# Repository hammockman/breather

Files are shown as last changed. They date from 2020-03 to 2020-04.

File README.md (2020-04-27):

This repository contains design details for a cheap easy to build and source ventilator.
this design was completed as part of competition in response to COVID-19 (see link below for competion info)
(https://www.agorize.com/en/challenges/code-life-challenge)

Since COVID-19 there have been a large increase in the number of open source ventilator designs. the links below are useful resources for someone who is wanting to design and or build an emergency ventilator in response to some sort of pandemic event such as COVID-19.

Links:

[Corona Virus Tech Handbook. Ventilator Chapter.] (https://coronavirustechhandbook.com/ventilators)

[Github Repository with a large number of existing design links] (https://github.com/eellak/covid19-open/blob/master/Hardware.md)

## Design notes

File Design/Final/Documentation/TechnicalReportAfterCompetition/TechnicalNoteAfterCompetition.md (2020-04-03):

---
title: "Manawa Ora"
subtitle: "Technical Note after Agorize submission"
author: [Manawa Ora team]
date: 2020-04-03
titlepage: true
toc: true
toc-own-page: true
tags: [ventilator, agorize]
...

# Summary

This note is a collection of documents that were part of the submission in the
Agorize Competition: "Code Life Ventilator Challenge". The team name for that
competition was *Manawa Ora*, and that name is also used herein for the team and
the design.

Our design goals were to make and design a simple ventilator that:

 - could be made anywhere in the world
 - used parts with supply chains outside the medical industry

Our main constraint was that we started the design only a couple of days before New
Zealand went into lock-down, and therefore only had the parts we'd bought the day
before stores closed.

The current version has the following "features":

 - 1" (25mm) BSP irrigation fittings provide gas conveyance, structural
   integrity, and sensor housing. These can be purchased from local suppliers in
   (plastic or stainless steel) or 3D-printed.

 - Air and oxygen flow are sensed using automotive Mass Air Flow Sensors. The
   ratio of these flows provides measurement of FiO2.

 - An expiration valve closes during inspiration and when expiration pressure
   falls below PEEP. High PEEP pressures can be provided by introducing small
   amounts of air via the inspriation valves.

 - The valving logic removes the need for a flap valve at the Y-piece.

 - Wireless communication of measured data and control commands. This allows for
   multiple viewers (e.g. tablet, PC, centralised PC, decentralised).

 - Filters and humidifier are separate units.

The design relies on the supply of clean compressed air and oxygen. This choice
has been made to a) keep the machine simple, and b) because we think large
gas banks and/or compressors are a more efficient way to supply several or many
ventilators.

\newpage
## Status

The prototype is built and satisfies most of the Agorize competition goals. It
is, however, not ready for production. The big picture of outstanding work follows:

Missing/incomplete feature | Difficulty
--|--
Add alarms to code and GUI | Simple
Sort required security for wireless communication and control | Depends on reuirements
Add correct fittings for hospital air/O2 supply | Simple
Improve flutter in valve control | Medium
Improve/test PEEP control when there is vacuum connected to expiration exhaust |Medium
Add a 230 v plug and main switch | Simple

Many of these aspects could be improved by having technical support from
appropriately trained and experienced medical personnel.

# Design

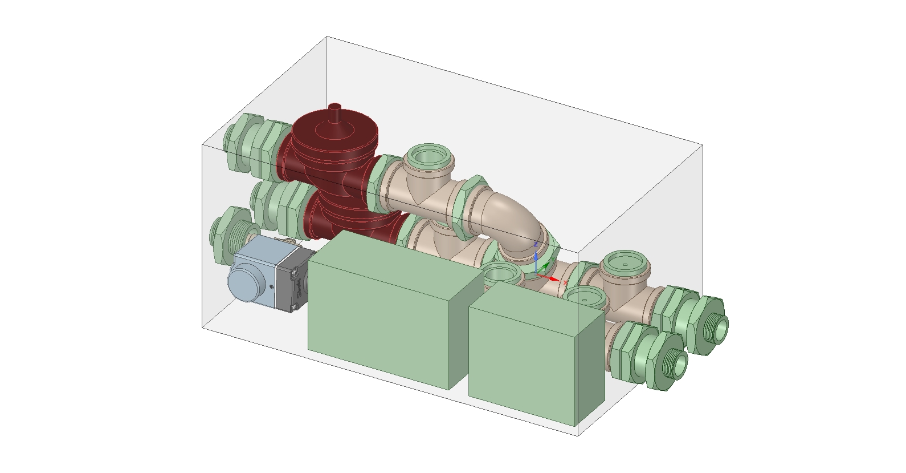
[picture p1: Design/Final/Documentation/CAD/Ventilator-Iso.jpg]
Isometric depiction of ventilator. The cabinet is semi-transparent, and the two ports on the front of the machine are the patient-side inspiration (right) and expiration (left) ports


Layout of the proposed ventilator

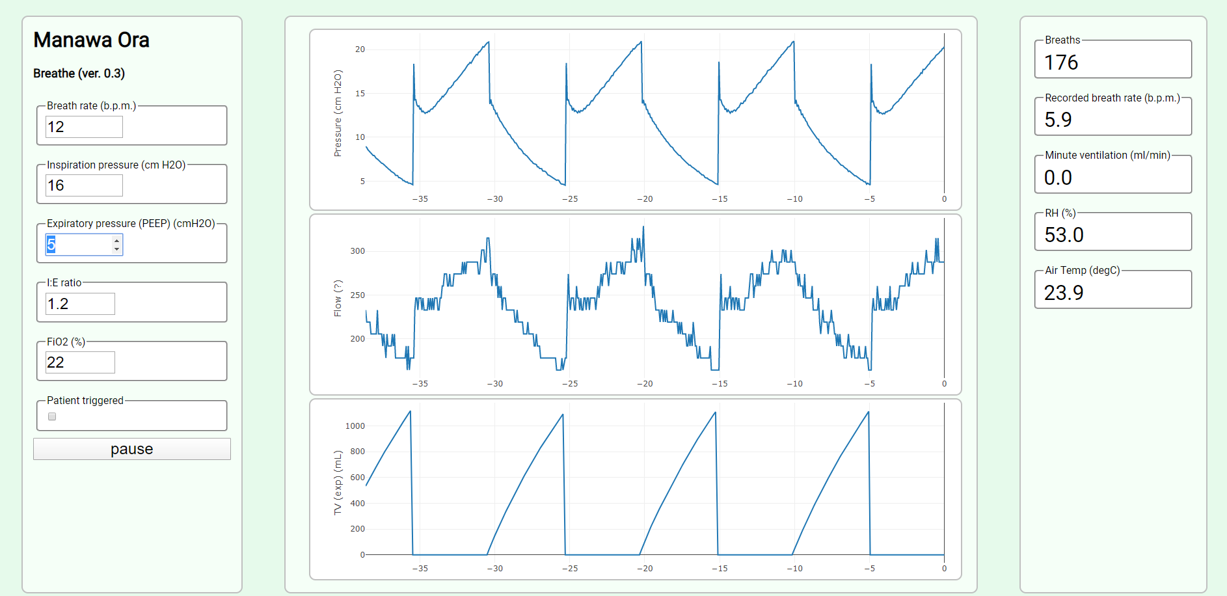
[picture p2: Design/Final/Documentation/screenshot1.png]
Operator user interface. The unit does not have any screen of it's own: it relies on wireless communication to other computers and devices.


# Prototype

The following two photos show the prototype that was made.

![Ventilator prototype. The rear of the machine is in the foreground: air inlet,
oxygen inlet, expriation exhaust. The middle ground shows the inspiration and
expiration conveyances, sensors, and electronics. In the background is the
tidal volume calibration (EasyYo) containers, the patient, and the bubble
humidifier. The patient is simulated by a dry bag restrained by a weighted and
sprung plywood hinge. Patient compliance is reduced by increasing the spring stiffness.](../system_with_pi1.jpg)

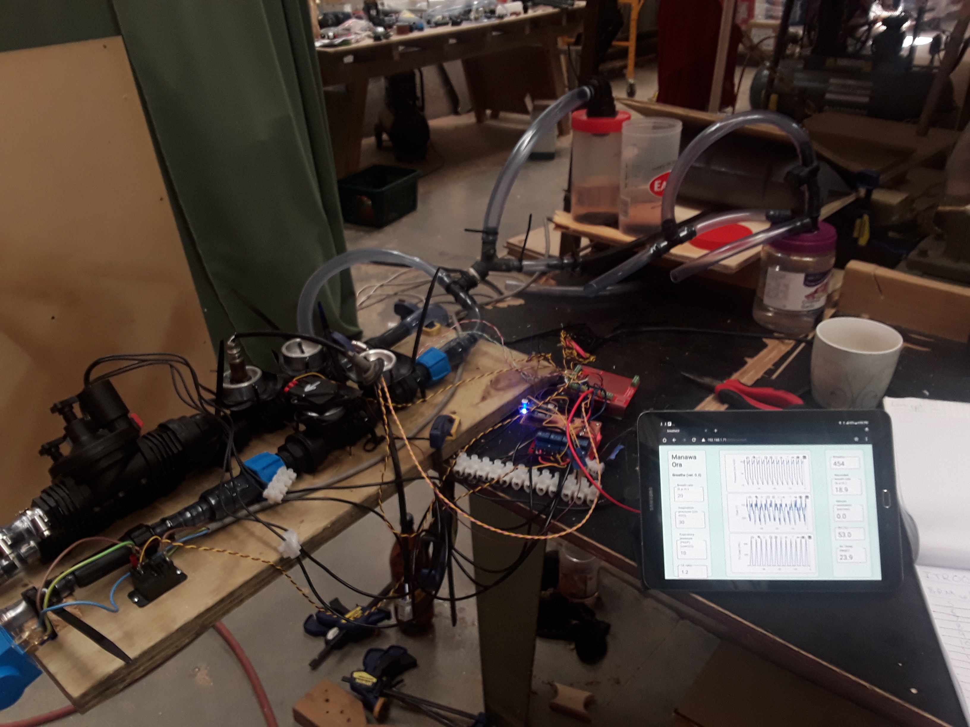
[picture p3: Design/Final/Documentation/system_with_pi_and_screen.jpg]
Operator interface on a tablet


\newpage
# Appendices

\newpage

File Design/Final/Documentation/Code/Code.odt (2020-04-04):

Manawa Ora software

## Overview and user guide

The Manawa-Ora codebase comprises two parts:

1. The User Interface software that allows the user to read and control the ventilator using a web browser. The browser can be on a tablet or central PC
2. The code on the mini-computer inside the ventilator is written using python. The software starts automatically and the normal user does not have to do any setup.

The user interface is shown below:

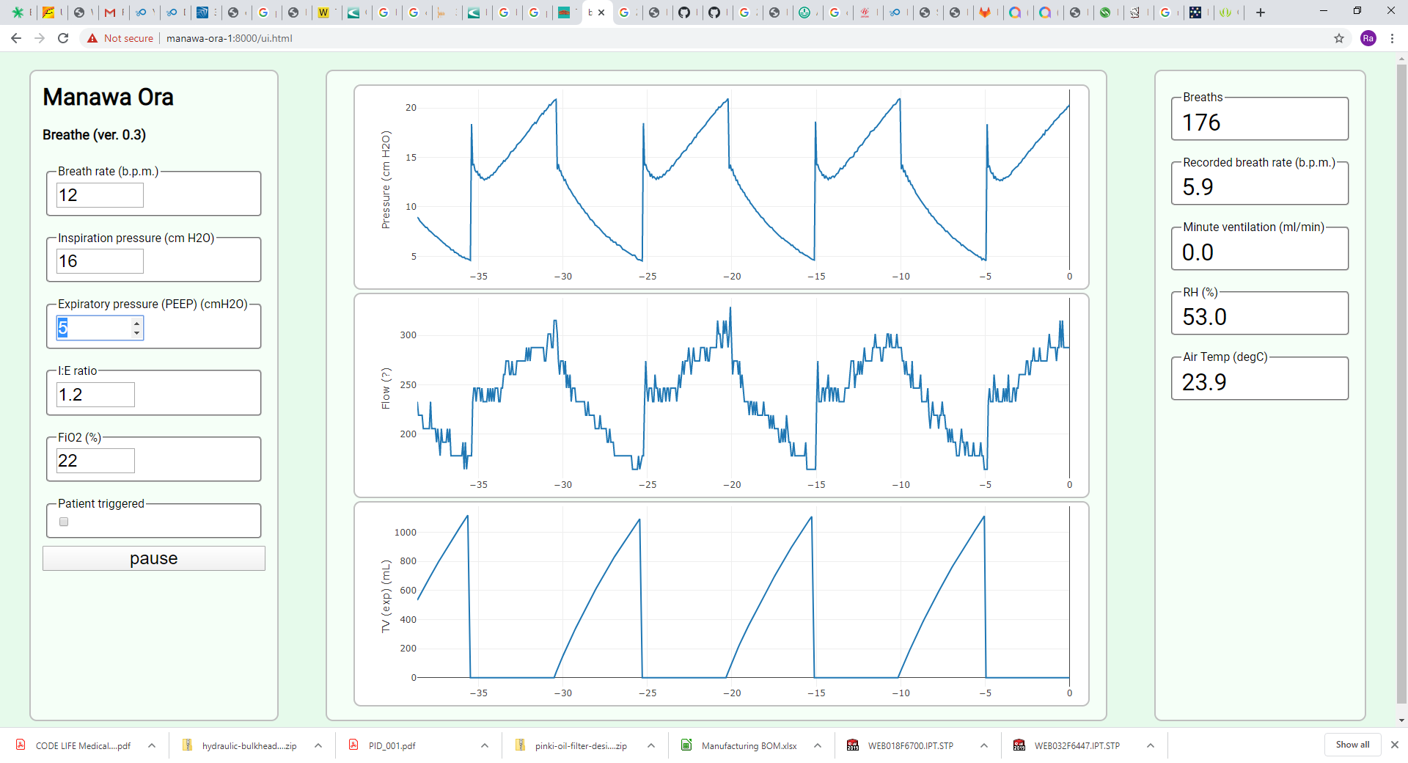
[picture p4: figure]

The operator can modify settings using the menu in the left panel. Resulting ventilation graphs and readings are shown in the centre and right hand panels.

# Installation

To install the ventilator for the first time the cabinet must be opened and an ethernet cable attached to the controller and a facility IT professional must assign the computer a static IP address: a ventilator ID should (preferably) be given as the machine hostname.

To install the User Interface software:

- The device browser, on a tablet or PC, needs to point to the IP address or hostname.

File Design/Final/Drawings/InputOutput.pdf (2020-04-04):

Sheet1

Page 1

Function | Tag | Instrument | I/O | PI address | Bus | PI Terminal
Inspiration pressure / temperature sensor | PT-011 | | | | I2C-1 | 3, 5
Temp / humidity sensor | HT-011 | | | | | 4
Expiration pressure / temperature sensor | PT-021 | | | | I2C-4 | 24,25
Air flow sensor | FT-011 | | analogue in | | A-D card | 3, 5
Oxygen flow sensor | FT-012 | | analogue in | | A-D card | 3, 5
Expiration flow sensor | FT-021 | | analogue in | | A-D card | 3, 5
Air inlet valve | SV-011 | R1 relay board | digital out | | | 17
Oxygen inlet valve | SV-012 | R2 relay board | digital out | | | 18
Expiration valve | SV-021 | R3 relay board | digital out | | | 25

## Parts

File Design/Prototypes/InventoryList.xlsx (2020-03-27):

Item Desc. | Part number | Domain | Supplier | Status | Quantity | unit price | cost | Puchased by
SG-5010 4.8-6V Servo Motor | SG-5010 | ` | Jaycar | received | 1 | 24.9 | 24.9 | JJ
2008 MAZDA 6 AIR FLOW METER |  | Sensor | maztech | awaiting delivery | 1 | 69 | 69 | JJ
2003 MAZDA MPV EGR VALVE |  | Sensor | maztech | awaiting delivery | 1 | 51.75 | 51.75 | JJ
2004 MAZDA 3 AIR CLEANER BOX |  | Filter | maztech | awaiting delivery | 1 | 46 | 46 | JJ
PVC Clear Tube - 7.9mm |  | Piping | irrigation express | awaiting delivery | 2 | 1.42 | 2.84 | JJ
PVC Clear Tube - 9.5mm |  | Piping | irrigation express | awaiting delivery | 2 | 2 | 4 | JJ
PVC Clear Tube - 13mm |  | Piping | irrigation express | awaiting delivery | 2 | 2.98 | 5.96 | JJ
PVC Clear Tube - 16mm |  | Piping | irrigation express | awaiting delivery | 2 | 3.82 | 7.64 | JJ
PVC Clear Tube - 19mm |  | Piping | irrigation express | awaiting delivery | 2 | 5.68 | 11.36 | JJ
PVC Clear Tube - 25mm |  | Piping | irrigation express | awaiting delivery | 2 | 9.38 | 18.76 | JJ
Antelco Lateral Tees - 13mm |  | Piping | irrigation express | awaiting delivery | 2 | 0.33 | 0.66 | JJ
Antelco Lateral Tees - 16mm |  | Piping | irrigation express | awaiting delivery | 2 | 0.78 | 1.56 | JJ
Antelco Lateral Tees - 19mm |  | Piping | irrigation express | awaiting delivery | 2 | 0.45 | 0.9 | JJ
Antelco Lateral Tees - 25mm |  | Piping | irrigation express | awaiting delivery | 2 | 0.92 | 1.84 | JJ
Antelco Lateral Tees 4mm - 10mm - 10mm |  | Piping | irrigation express | awaiting delivery | 2 | 0.92 | 1.84 | JJ
Antelco Lateral Valves (Green Back) - 16mm |  | Piping | irrigation express | awaiting delivery | 3 | 2.46 | 7.38 | JJ
Dripline Ratchet Clip 16mm |  | Piping | irrigation express | awaiting delivery | 12 | 0.24 | 2.88 | JJ
Norma 9mm S/Steel Band Worm Drive Hose Clamps - 8mm - 12mm |  | Piping | irrigation express | awaiting delivery | 8 | 1.9 | 15.2 | JJ
Norma 9mm S/Steel Band Worm Drive Hose Clamps - 16mm - 25mm |  | Piping | irrigation express | awaiting delivery | 8 | 1.9 | 15.2 | JJ
Dripline to Lateral Reducing Joiner - 16mm/13mm |  | Piping | irrigation express | awaiting delivery | 4 | 0.47 | 1.88 | JJ
Dripline to Lateral Reducing Joiner - 19mm/16mm |  | Piping | irrigation express | awaiting delivery | 4 | 0.47 | 1.88 | JJ
Dripline to Lateral Reducing Joiner - 25mm/16mm |  | Piping | irrigation express | awaiting delivery | 4 | 1.08 | 4.32 | JJ
16mm Dripline Elbow |  | Piping | irrigation express | awaiting delivery | 2 | 0.28 | 0.56 | JJ
Lateral Inline Screen Filter - 13mm - 19mm - 16mm |  | Piping | irrigation express | awaiting delivery | 2 | 5.19 | 10.38 | JJ
50mm Plastic display side entry 8mm Pressure Gauge - 35psi 2.5Bar plastic side entry Pressure Gauge |  | Piping | irrigation express | awaiting delivery | 1 | 8.5 | 8.5 | JJ
Hansen Reducing Bush - 15mm/8mm |  | Piping | irrigation express | awaiting delivery | 1 | 1.85 | 1.85 | JJ
Antelco Female Threaded Tee - Threaded Tee - 13mm Barbs x 15mm BSPF |  | Piping | irrigation express | awaiting delivery | 1 | 2.01 | 2.01 | JJ
Antelco Female Threaded Tee - Threaded Tee - 19mm Barbs x 15mm BSPF |  | Piping | irrigation express | awaiting delivery | 1 | 1.66 | 1.66 | JJ
Antelco Female Threaded Tee - Threaded Tee - 25mm Barbs x 15mm BSPF |  | Piping | irrigation express | awaiting delivery | 1 | 1.87 | 1.87 | JJ
MULTICOMP HCZ-D5-A Humidity Sensor, HCZ Series, 20% to 90% RH, 5 %, Through Hole, Enclosed |  | Sensor | element 14 | awaiting delivery | 2 | 9.98 | 19.96 | JJ
OMRON 2SMPP-02 Pressure Sensor, MEMS, Air, 0 to 50°C, 37 kPa, Voltage, Gauge, Hose / Tube, 100 µA |  | Sensor | element 14 | awaiting delivery | 4 | 5.16 | 20.64 | JJ
MULTICOMP PRO MC6A-7/0.2T2-PK-100M Wire, Stranded, Equipment, 7/0.2 mm Type 2, Per Metre, PVC, Pink, 0.22 mm² |  | Wiring | element 14 | awaiting delivery | 5 | 0.301 | 1.505 | JJ
MULTICOMP PRO MC6A-7/0.2T2-BN-100 Wire, Stranded, Equipment, 7/0.2 mm Type 2, Per Metre, PVC, Brown, 0.22 mm² |  | Wiring | element 14 | awaiting delivery | 5 | 0.301 | 1.505 | JJ
MULTICOMP PRO MC6A-7/0.2T2-YW-100 Wire, Stranded, Equipment, 7/0.2 mm Type 2, Per Metre, PVC, Yellow, 0.22 mm² |  | Wiring | element 14 | awaiting delivery | 5 | 0.301 | 1.505 | JJ
MULTICOMP PRO MC6A-1/0.6T2-PK-100 Wire, Solid, Equipment, Per Metre, PVC, Pink, 23 AWG, 0.28 mm² |  | Wiring | element 14 | awaiting delivery | 5 | 0.378 | 1.89 | JJ
MULTICOMP PRO MC6A-1/0.6T2-YW-100 Wire, Solid, Equipment, Per Metre, PVC, Yellow, 23 AWG, 0.28 mm² |  | Wiring | element 14 | awaiting delivery | 10 | 0.356 | 3.56 | JJ
Fuel filter inline 3/8 |  | Filter | BNT | received | 2 | 18 | 36 | RC
240v washing machine solenoid valve |  | Valve | Philip smith | received | 1 | 25 | 25 | RC
240v refrigerant solenoid valve |  | Valve | Philip smith | received | 1 | 145 | 145 | RC
Air flow sensor |  | Sensor | Repco | received | 1 | 252.75 | 252.75 | RC
Vacuum hose t-junction 10mm |  | Piping | Repco | received | 2 | 10.87 | 21.74 | RC
Oxygen sensor |  | Sensor | Repco | received | 1 | 93 | 93 | RC
Temp/Humidity sensor |  | Sensor | Jaycar | received | 1 | 11.9 | 11.9 | RC
Laser diode |  | Sensor | Jaycar | received | 1 | 6.9 | 6.9 | RC
Digital barometric pressure sensor |  | Sensor | Jaycar | received | 2 | 22.9 | 45.8 | RC
Battery SLA 12v 6Ah |  | Battery | Jaycar | received | 1 | 36.9 | 36.9 | RC
DC-DC voltage regulator (variable) |  | Electronics | Jaycar | received | 1 | 10.9 | 10.9 | RC
Relay board 5V |  | Electronics | Jaycar | received | 2 | 6.9 | 13.8 | RC
Relay board 4 ch 12v |  | Electronics | Jaycar | received | 1 | 17.9 | 17.9 | RC
Raspberry Pi 3B+ |  | Electronics | Jaycar | received | 1 | 99.9 | 99.9 | RC
Raspberry Pi prototyping shield |  | Electronics | Jaycar | received | 1 | 17.9 | 17.9 | RC
Raspberry Pi touch LCD |  | Electronics | Jaycar | received | 1 | 56.9 | 56.9 | RC
Raspberry Pi GPIO expansion |  | Electronics | Jaycar | received | 1 | 16.9 | 16.9 | RC
PCB prototyping board |  | Electronics | Jaycar | received | 2 | 5.9 | 11.8 | RC
Air hose 10mm |  | Piping | Tradezone | received | 2 | 5 | 10 | RC
Pneumatic T-junctions 10mm |  | Piping | Tradezone | received | 4 | 2 | 8 | RC
12V 25mm normally closed solenoid valves (SV25-12) |  | Valve | The Water Sprinkler Shop | awaiting delivery | 2 | 30.36 | 60.72 | JH
12V 25mm latching/pulse valves (SV25L) |  | Valve | The Water Sprinkler Shop | awaiting delivery | 2 | 36.68 | 73.36 | JH
12V Solenoid Coil (SC2-12) |  | Valve | The Water Sprinkler Shop | awaiting delivery | 2 | 15.39 | 30.78 | JH
25mm BSP Female Elbow (7208/25) |  | Piping | The Water Sprinkler Shop | awaiting delivery | 8 | 2.25 | 18 | JH
25mm BSP Female Tee (T25F) |  | Piping | The Water Sprinkler Shop | awaiting delivery | 6 | 2.97 | 17.82 | JH
25mm BSP Male Nipple (NP-25) |  | Piping | The Water Sprinkler Shop | awaiting delivery | 12 | 0.91 | 10.92 | JH
25mm-15mm BSP Reducing Male Nipple (?) |  | Piping | The Water Sprinkler Shop | awaiting delivery | 3 | 2.15 | 6.45 | JH
12V Airtac Solenoid valve | 4V110-06 | Valve | Edwin | received | 5 | ?? |  | Edwin
One touch plastic pneumatic fitting t type 6mm quick tube connector air 3 way PE-6 union pipe joint |  | Piping | Aliexpress | received | 10 | ?? | ?? | Edwin
Air Pneumatic 10mm Hose Tube ??? Male Thread Air Pipe Connector Quick Coupling Brass Fitting |  | Piping | Aliexpress | received | 10 | ?? | ?? | Edwin
Potter and Brumfield 12 V relay NO and NC 230 V contacts | T9AP5D52-12 | Electronics | ?? | received | 2 | ?? | ?? | Edwin
Potter and Brumfield 12 V relay NO 230 V contacts | T9AP1D52-12 | Electronics | ?? | received | 2 | ?? | ?? | Edwin
12V relay from the dark ages with 4 sets of contacts |  | Electronics | ?? | received | 1 | ?? | ?? | Edwin

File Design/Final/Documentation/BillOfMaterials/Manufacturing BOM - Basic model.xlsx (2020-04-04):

MANUFACTURING BOM – Basic model
ITEM | DESCRIPTION | PART NUMBER | QTY | UNIT COST | NZ SUPPLIER | PRICE (NZD) | Price (USD) | Supply industry
1 | 25mm BSP Female Tee | (T25F) | 3 | 2.97 | The Water Sprinkler Shop | 8.91 | 5.35 | Irrigation/plumbing
2 | 25mm BSP Female Elbow | (7208/25) | 2 | 2.25 | The Water Sprinkler Shop | 4.50 | 2.70 | Irrigation/plumbing
3 | 25mm BSP Male Nipple | (NP-25) | 6 | 0.91 | The Water Sprinkler Shop | 5.46 | 3.28 | Irrigation/plumbing
4 | 12V 25mm normally closed solenoid valves | (SV25-12) | 2 | 30.36 | The Water Sprinkler Shop | 60.72 | 36.43 | Irrigation/plumbing
5 | 25x15mm Reducing Bush | HRB2515 | 4 | 1.77 | Irrigation Express | 7.08 | 4.25 | Irrigation/plumbing
6 | Tank fittings | HTFFT25 | 4 | 7.41 | Irrigation Express | 29.64 | 17.78 | Irrigation/plumbing
7 | Solenoid valve, EVR 6 - normally open | 032L8085 | 1 | 72.5 | Philip Smith | 72.50 | 43.50 | Electrical supplies
8 | Solenoid coil, BE230AS | 018F6701 | 1 | 72.5 | Philip Smith | 72.50 | 43.50 | Electrical supplies
9 | Large particle filter | 8-16/9W4P | 1 | 1.9 | Irrigation Express | 1.90 | 1.14 | Irrigation/plumbing
10 | Temp/Humidity sensor | DHT12 | 1 | 14.9 | Jaycar | 14.90 | 8.94 | Electronic supplies
11 | Digital barometric pressure sensor | BMP180 | 2 | 22.9 | Jaycar | 45.80 | 27.48 | Electronic supplies
12 | Raspberry Pi 3B+ | 3B+ | 1 | 65 | Jaycar | 65.00 | 39.00 | Electronic supplies
13 | Raspberry Pi shield and ADC | XC9050 | 1 | 17.9 | Jaycar | 17.90 | 10.74 | Electronic supplies
14 | Raspberry Pi GPIO expansion | XC9040 | 1 | 16.9 | Jaycar | 16.90 | 10.14 | Electronic supplies
15 | Relay board 4 ch 12v | XC4419 | 1 | 17.9 | Jaycar | 17.90 | 10.74 | Electronic supplies
16 | PS with battery SLA 12v 6Ah | SB2485 | 1 | 36.9 | Jaycar | 36.90 | 22.14 | Electronic supplies
17 | DC-DC voltage regulator (variable) | XC4514 | 1 | 10.9 | Jaycar | 10.90 | 6.54 | Electronic supplies
18 | Fuelmiser Air Flow Sensor | VDO - CAF034 | 2 | 40 | Repco | 80.00 | 48.00 | Automotive parts warehouse
19 | Cabinet | 22” toolbox | 1 | 30 | Bunnings | 40.00 | 24.00
 |  |  |  | Total cost |  | 609.41 | 365.65

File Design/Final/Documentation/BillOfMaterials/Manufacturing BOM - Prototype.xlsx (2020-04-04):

MANUFACTURING BOM – Prototype as built
ITEM | DESCRIPTION | PART NUMBER | QTY | UNIT COST | NZ SUPPLIER | PRICE (NZD) | Price (USD)
1 | 25mm BSP Female Tee | (T25F) | 3 | 2.97 | The Water Sprinkler Shop | 8.91 | 5.35
2 | 25mm BSP Female Elbow | (7208/25) | 1 | 2.25 | The Water Sprinkler Shop | 2.25 | 1.35
3 | 25mm BSP Male Nipple | (NP-25) | 5 | 0.91 | The Water Sprinkler Shop | 4.55 | 2.73
4 | 25mm Hex Screw Plug | HSP25 | 3 | 0.87 | Irrigation Express | 2.61 | 1.57
5 | 12V 25mm normally closed solenoid valves | (SV25-12) | 2 | 30.36 | The Water Sprinkler Shop | 60.72 | 36.43
6 | 15x6mm Reducing Bush | HRB1506 | 2 | 1.19 | Irrigation Express | 2.38 | 1.43
7 | 25x15mm Reducing Bush | HRB2515 | 5 | 1.77 | Irrigation Express | 8.85 | 5.31
8 | 15mm Male Hose Tail | HHT15 | 3 | 2.13 | Irrigation Express | 6.39 | 3.83
9 | 16mm End Plug | LEP16 | 1 | 1.16 | Irrigation Express | 1.16 | 0.70
10 | 16mm Lateral Inline Filter | LILF16 | 2 | 5.19 | Irrigation Express | 10.38 | 6.23
11 | Solenoid valve, EVR 6 - normally open | 032L8085 | 1 | 72.5 | Philip Smith | 72.50 | 43.50
12 | Solenoid coil, BE230AS | 018F6701 | 1 | 72.5 | Philip Smith | 72.50 | 43.50
13 | PVC Clear Tube - 16mm - per meter | PVC-30-1016 | 1 | 3.82 | Irrigation Express | 3.82 | 2.29
14 | 8mm – 16mm Worm Drive Hose Clamp | 8-16/9W4P | 2 | 1.9 | Irrigation Express | 3.80 | 2.28
15 | Norma 9mm S/Steel Hose Clamps – 16mm-25mm | 16-25/9W4P | 12 | 1.9 | Irrigation Express | 22.80 | 13.68
16 | Mechpro Connector 1/4in M | MPC14M | 3 | 6.49 | Repco | 19.47 | 11.68
17 | O2 Sensor | AFR722-EE26 | 1 | 93 | Repco | 93.00 | 55.80
18 | Temp/Humidity sensor | DHT11 | 1 | 11.9 | Jaycar | 11.90 | 7.14
19 | Digital barometric pressure sensor | BMP180 | 2 | 22.9 | Jaycar | 22.90 | 13.74
20 | Raspberry Pi 3B+ | 3B+ | 1 | 99.9 | Jaycar | 99.90 | 59.94
21 | Raspberry Pi shield and ADC | XC9050 | 1 | 17.9 | Jaycar | 17.90 | 10.74
22 | Raspberry Pi GPIO expansion | XC9040 | 1 | 16.9 | Jaycar | 16.90 | 10.14
23 | Relay board 4 ch 12v | XC4419 | 1 | 17.9 | Jaycar | 17.90 | 10.74
24 | Battery SLA 12v 6Ah | SB2485 | 1 | 36.9 | Jaycar | 36.90 | 22.14
25 | DC-DC voltage regulator (variable) | XC4514 | 1 | 10.9 | Jaycar | 10.90 | 6.54
26 | Fuelmiser Air Flow Sensor | VDO - CAF034 | 1 | 252.75 | Repco | 252.75 | 151.65
 |  |  |  | Total cost |  | 884.04 | 530.42

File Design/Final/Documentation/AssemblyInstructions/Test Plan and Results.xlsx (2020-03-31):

Inspection Test Plan
Date Created | 2020-01-31
Project | Ventilator
Created By | Joseph Jury
Item |  | Completed By | Witnessed By | Date | Reference Documents | Results | Notes

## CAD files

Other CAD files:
Design/Final/Drawings/VentElec1.dwg

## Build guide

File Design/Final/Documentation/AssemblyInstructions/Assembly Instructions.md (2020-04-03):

# Assembly instructions

1.  Assemble pipe fittings and solenoid valves for inspiratory line as
    per MO-GA001. Take care to ensure thread tape is used on all male
    threads. Tighten fittings hand tight and then a further 3/4 turn or
    more using a spanner.

2.  Assemble pipe fittings and solenoid valve for expiratory line as per
    MO-GA001. Take care to ensure thread tape is used on all male
    threads. Tighten fittings hand tight and then a further 3/4 turn or
    more using a spanner.

3.  Lower expiratory line into housing. Mount tank fittings onto housing
    and expiratory line as per MO-GA001.

4.  Lower inspiratory line into housing. Mount Tank fittings onto
    housing and inspiratory line as per MO-GA001.

5.  Mount all sensors in T-junctions as per MO-GA001 & MO-PID-001.
    Ensure sensors are mounted using correctly modified 1" BSP blanking
    plugs.

6.  Mount 'raspberry pi controller', '12V Relay Board', '12-5V DC-DC'
    converter and '230V AC 12V DC UPS' as per MO-E-001

7.  Mount the above electrical controls into ventilator housing as per
    MO-GA001

1.  Connect solenoid valves and flow sensors to 12V Relay Board as per
    MO-E-001 & MO-PID-001

2.  Connect humidity and pressure sensors to 5V rail on Raspberry Pi
    Controller as per MO-E-002 & MO-PID-001

3.  Once device has been fully assembled. Consult MO-ITP-001 for Factory
    acceptance testing

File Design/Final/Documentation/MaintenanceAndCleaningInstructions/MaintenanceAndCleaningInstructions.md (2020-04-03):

# Maintenance and cleaning instructions

Cleaning
========

Exterior
--------

1.  Disconnect hoses and filters
2.  Wipe the outside of the cabinet with a damp clean cloth. Light
    solvents and detergents may be used

Interior
--------

1.  Clean the exterior, do not connect hoses until interior cleaning is
    complete
2.  Connect a 22mm hose to the expiration connector on the front of the
    unit
3.  Connect the expiration connector at the rear of the unit to a
    watertight receptacle
4.  If a flow sensor is fitted to the expiration channel (this is an
    optional extra), then this sensor must be removed prior to the
    following step. Also prior to the following step, screw the supplied
    blind fitting in place of the flow sensor.
5.  Flush ten (10) litres of water-disinfectant solution through, from
    the front to the rear, of the expiration channel
6.  NEVER FLUSH LIQUIDS THROUGH THE INSPIRATION SIDE OF THE MACHINE.

Maintenance
===========

1.  The filters and humidifier are external to the unit and should be
    maintained/replaced as required by the manufacturer
2.  The 12v solenoids should be replaced every 4000 hours.

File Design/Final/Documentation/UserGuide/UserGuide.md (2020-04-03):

--var fio2: FiO<sub>2</sub>
--var vent: Manawa Ora

# {{vent}} User Guide

## Revision History

| Version | Date | Author(s) |
| ------- | ---- | ----------|
| v0.1 | 01/04/20 | JH, RC, JJ, MO |

## Contact Details

**Manawa Ora**
385 State Highway 33
Mourea
Rotorua 3074
New Zealand

Customer Care:
manawaoraservice@aliente.ch

## Warranty

There are no warranties expressed or implied.

Manawa Ora shall not be liable for loss of profits, loss of use, consequential damages, or any other
claim based on breach of warranty. Manawa Ora liability for damages of any kind shall be limited to the
purchase price of the defective unit.

## Notices

The {{vent}} ventilator complies with XXX. It does however use and radiate radio frequency energy.

The function of this machine may be adversely affected by the operation of other nearby equipment, such as high frequency surgical diathermy equipment, short-wave therapy equipment, defibrillators, or MRI equipment.

The {{vent}} ventilator may emit and receive electromagnetic interference. Avoidance of this exposure is recommended whenever possible.

The {{vent}} ventilator is not suitable for use in shielded magnetic scanners.

> ** Notice To Operators**
>
> **Unsafe Operation** - Operating the {{vent}} ventilator without a complete and thorough understanding of its attributes is unsafe and may cause harm to the patient. It is important that this manual be read and understood in its entirety before operating the ventilator.
> **Warnings and Cautions Section** - Read the section on Warnings and Cautions carefully before operating the {{vent}} ventilator.
> **Use and Maintenance** - Any questions regarding installing, operating, or maintaining the {{vent}} ventilator, should be directed to a certified Manawa Ora service technician or Manawa Ora.

## Contents

## 1 Introduction

This Operator’s Manual contains detailed information and instructions which when adhered to ensure the safe and effective set up, use and simple maintenance of the {{vent}} ventilator.

This manual is designed for use by Respiratory Therapists or other qualified and trained personnel
under the direction of a physician and in accordance with applicable state laws and regulations. It
contains the following:

* Ventilator Overview
* Installation and Checkout
* Using the Controls and Indicators
* Monitored Data
* Ventilator Alarms
* Extended Features
* Ventilator Checkout tests
* Operating Procedure
* Troubleshooting
* Cleaning, Disinfecting and Sterilizing
* Set Up / Maintenance
* Power and Battery Operation 

### WARNINGS

**Untrained Personnel** Only properly trained personnel should operate the ventilator. The {{vent}} ventilator is a restricted medical device designed for use by Respiratory Therapists or other properly trained and qualified personnel under the direction of a physician and in accordance with applicable laws and regulations.

**Leak Testing the Patient Breathing Circuit** The patient circuit must be leak tested before connection to the patient. In addition, correct operation of the ventilator alarm, displays and controls should also be checked. Harm to the patient or ineffective ventilation may result from failure to leak test the patient breathing circuit before connection to a patient.

**Adjustable and Critical Alarms** For safety purposes, all adjustable alarms and all critical alarms must be checked to insure proper operation.

**Alarms Function Verification** All alarms must be verified as functioning properly on a daily basis. If any alarm malfunctions, immediately contact Manawa Ora.

**Patient Monitoring** Patients who are dependent on a ventilator should be constantly monitored by qualified personnel. Such personnel should be prepared to address equipment malfunctions and circumstances where equipment becomes inoperative. An alternative method of ventilation should be available for all patients dependent on the ventilator, and qualified personnel should be fully familiar with emergency ventilation procedures.

**Alternative Ventilation** It is recommended that an alternative means of ventilating the patient be available at all times and that all ventilator operators be fully familiar with emergency ventilation procedures.

**Fire or Explosion** Operation of the {{vent}} ventilator in the presence of flammable gases could cause a fire or explosion. Under no circumstances is the ventilator to be operated when explosive gases are present. The presence of nitrous oxide or flammable anesthetics presents a danger to the patient and operator.

**Patient Breathing Circuit Disconnection** Inadvertent disconnection of the patient from the patient breathing circuit can be dangerous.

<!--
**Critical Alarms**  Failure to set the critical alarms such as the Low Minute Volume alarm and the Low Pressure alarm may cause non-detection (no alarm) for a disconnection of the lower sense line or the 
exhalation valve drive line.

**Exhalation Valve Diaphragm** Patient ventilation may be ineffective or dangerous if the exhalation
valve diaphragm is damaged or worn out. The exhalation valve diaphragm must be inspected on a
daily basis and replaced whenever necessary.
Sustained HIGH PRES Alarm - During a sustained High Pressure alarm condition (HIGH PRES), the
ventilator’s turbine is stopped and gas is not delivered to the patient. Disconnect the patient from the
ventilator and ventilate the patient using an alternative method. See Chapter 15 - Troubleshooting,
Alarms for additional information concerning the HIGH PRES alarm.
BAT EMPTY Alarm - A BAT EMPTY alarm indicates the internal battery is almost depleted. Connect
the ventilator to an external power source immediately. 
Battery run time - When the battery reaches the BAT LOW level, the ventilator will only run for
approximately 10 minutes before generating a battery empty alarm (BAT EMPTY). The approximate
time shown is based on tests using the nominal settings, a new battery and a full 8 hour charge cycle
as specified in Appendix A - Ventilator Specifications. Actual run time may be more or less depending
on ventilator settings, patient demand, and battery age or condition. It is highly recommended that an
alternate power source is connected PRIOR to the ventilator reaching the BAT EMPTY alarm
condition to ensure continuous, uninterrupted patient ventilation
INOP Alarm - If an INOP alarm occurs during operation, ventilate the patient using an alternative
method, disconnect the ventilator, and immediately contact a certified CareFusion service technician
or CareFusion.
NO CAL Condition - Operation of the LTV®
 1200 / 1150 ventilator under a NO CAL condition may
result in inaccurate pressure and volume measurements. Should this condition occur, disconnect the
patient from the ventilator, provide an alternative method of ventilation and immediately contact a
certified CareFusion service technician or CareFusion.
XDCR FAULT Alarm - Continued operation of the LTV®
 1200 / 1150 ventilator with an activated
XDCR FAULT alarm may result in inaccurate flow and volume measurements. Should this condition
occur, disconnect the patient from the ventilator, provide an alternative method of ventilation and
immediately contact a certified CareFusion service technician or CareFusion.
Personal Injury and Electric Shock - Operation of the LTV®
 1200 / 1150 ventilator if any of its
panels have been removed may result in electrical shock to the patient or operator. All servicing must
be performed by a certified CareFusion service technician.
Audible Alarms - Failure to immediately identify and correct audible alarm situations may result in
serious patient injury.
Equipment Malfunction or Failure - The LTV®
 1200 / 1150 ventilator has alarms to notify operators
of certain conditions and to cease operating upon detecting possible danger. In the event of
equipment failure, all ventilator operators should have an alternative method of ventilation available
and be fully familiar with emergency ventilation procedures.
Improperly Functioning Ventilator - Operation of a ventilator that does not appear to be working
properly may be hazardous. If the ventilator is damaged, fails Ventilator Checkout tests or
malfunctions in any way, discontinue its use and immediately contact a certified CareFusion service
technician or CareFusion.
Ventilator Checkout Tests – Be aware that gas is not delivered to the patient during these tests.
Disconnect the patient from the ventilator and ventilate the patient using an alternative method before
running the Ventilator Checkout tests.
Ventilator Checkout and Maintenance Modes - The LTV®
 1200 / 1150 ventilator does not deliver
gas during the Ventilator Checkout mode (VENT CHECK) or Ventilator Maintenance mode (VENT
MTNCE) and should not be used to ventilate a patient during these tests.
Inspired Oxygen (FIO2) Concentration – If the patient has a variable respiratory rate, his/her minute
ventilation will fluctuate. If exact concentrations of inspired oxygen (FIO2) are required to be delivered
to the patient, it is recommended that an accurate oxygen analyzer with alarms be used.
O2 Cylinder Duration Information (LTV®
 1200 only) - The accuracy of the displayed useable
amount of oxygen remaining in an external O2 cylinder (O2 DUR hh:mm) is dependant on the
precision of the pressure gauge used on the O2 cylinder and the accuracy of the information provided
by the operator in the O2 CYL DUR menu settings. The calculated/displayed useable amount of
oxygen information is to be used for reference purposes only. 

Ventilation Variables and O2 Consumption - Variations in the patient’s minute ventilation, I:E ratio
and/or ventilator setting changes or equipment status (i.e. circuit leaks) affect the consumption rate of
oxygen. When warranted by a patients condition, it is recommended that a back-up cylinder or
alternative source of oxygen be available at all times.
Before Using Automobile Cigarette Lighter or Power Outlets - Before using Automobile Cigarette
Lighter or Power Outlets as a power source for the LTV®
 1200 / 1150, assure that the ventilator’s
internal battery is in good condition and fully charged. Poor cigarette lighter or power outlet
connections, electrical system defects (battery, charging system, etc.), or use of vehicle accessories
(air conditioner, high current lights, high power audio equipment, etc.) could result in less than the
required voltage being delivered to the ventilator, generate a POWER LOST alarm and switch the
ventilator’s power source to the internal battery.
Unauthorized Parts or Accessories – Serious harm to the patient may result from the use of
unauthorized parts or accessories. Only items expressly approved by CareFusion may be used in
conjunction with the LTV®
 1200 / 1150 ventilators.
Unapproved Adapters – Only CareFusion Accessories should be used to connect the ventilator to
Patient Assist Call Systems. These accessories incorporate safety features to reduce the risk of
shock. Do not attempt to modify these accessories in any way.
Patient Assist Call Connector – Do not apply more than 25V rms or 32VDC to the Patient Assist
Call connector.
Ventilator Service and Repair - All servicing or repair of the LTV®
 1200 / 1150 ventilator must be
performed only by a service technician certified by CareFusion.
Patient Circuits – CareFusion Patient Circuits, Exhalation Valve Assemblies and Water Traps are
shipped clean, not sterile.
Ultra Violet Light Sensitivity – The material used in the tubing of the Reusable Patient Circuits is
not UV stable. Avoid exposure of the tubing to UV light.
Mounting Screws - Refer to the information contained in CareFusion Replacement Screws Kit, P/N
11149, to determine the appropriate accessories mounting screws or accessories replacement
screws location, type and length to use when removing or exchanging external accessories on an
LTV®
 ventilator.
Mounting Screw Use – Internal damage to the ventilator may result if the wrong length mounting
screws are used when installing or removing external accessories.
Patient Circuit Accessories - The use of accessories such as Speaking Valves, Heat-Moisture
Exchangers and Filters create additional patient circuit resistance and in the event of a disconnection,
may impede the generation of a Low Pressure alarm. Ensure that the Low Pressure alarm settings
accommodate these types of accessories when used in combination with patient circuits.
Low Minute Volume Control Settings - The Low Min. Vol. control should be set to its highest
clinically appropriate value. If there is a clinical need to set the Low Minute Volume alarm to lower
values or off (“- - -“), perform a clinical assessment to determine if an alternative monitor (i.e. a Pulse
Oximeter with an audible alarm, or a Cardio Respiratory Monitor) should be used.
The MR Conditional LTV®
 1200 System is specified as - An LTV®
 1200 Ventilator (P/N 18888-
2XX), LTV®
 1200 MR Safe 15ft Patient Circuit (P/N 19189-001), MR Conditional Floor Stand (P/N
14982-001), and a LTV®
 AC adapter (P/N 18053-001). Adding not approved parts or accessories may
cause patient and/or operator harm. 
-->

### Cautions

<!--
CAUTION
Ventilator Sterilization – To avoid irreparable damage to the LTV®
 1200 / 1150 ventilator, do not
attempt to sterilize it.
Cleaning Agents – To avoid damaging the ventilator’s plastic components and front panel, do not
use cleaning agents containing ammonium chloride, other chloride compounds, more than 2%
glutaraldehyde, phenols, or abrasive cleaners.
Ventilator Immersion - Do not immerse the ventilator in liquids.
Reusable Patient Circuit Components - To avoid degradation of the reusable patient circuit
components, do not exceed the following constraints:
 50 cleaning cycles or 1 year (whichever comes first)
Steam Autoclave:
 Pressure: 20 PSIG
 Temperature: 275°F (135°C)
 Time: 6 minutes
Liquid Sterilizing Agent:
Do not use any of the following solutions to clean, disinfect, or sterilize the patient circuit:
Pasteurization:
 A 30-minute warm water detergent and a 30-minute 165°F (74°C) hot water cycle.
 Drying in a sterile drier for more than 1 hour or 140°F (59°C).
Gas (ETO):
 Temperature: 131°F (55°C)
Differential Pressure Ports - A low pressure air nozzle with flow less than 10 liters per minute
should be used for cleaning the differential pressure ports.
Exhalation Valve Cleaning - Do not pour or spray liquid cleaners into the exhalation valve.
Patient Wye Installation – After cleaning, install the patient wye in the patient circuit so the proximal
sense lines are oriented up while operating. 
Care of the Exhalation Valve - The exhalation valve is a delicate assembly and may be damaged if;
 Care is not exercised when handling or cleaning it.
 Cleaning instruments or foreign bodies are inserted into it.
 High-pressure gas nozzles are used to dry it.
Front Panel Cleaning – Do not pour or spray liquid cleaners onto the front panel.
Care of Bacterial Filters – If bacterial filters are used in conjunction with the LTV®
 1200 / 1150
ventilator, comply with all procedures as specified by the filter manufacturer.
Wet or Damp Filters - Do not install a wet or damp filter into the LTV®
 1200 / 1150 ventilator. This
could damage the ventilator.
Oxygen Supply Contamination - The accuracy of the oxygen delivery capabilities of LTV®
 1200 /
1150 ventilator can be compromised by foreign debris contamination in the oxygen supply system. To
reduce the risk of airborne contaminants entering the ventilator, ensure that any oxygen supply
connected to the ventilator is clean, properly filtered1
 and that the ventilator’s O2 Inlet Port Cap is
securely installed on the O2 Inlet Port whenever the ventilator is not connected to an external oxygen
supply.
Proximal Sense Lines - Do not remove the proximal sense lines from the patient wye.
Automobile Cigarette Lighter and Power Outlets – Automobile cigarette lighter and power outlets
are normally wired for a positive center contact and ground sleeve contact. Connecting the ventilator
to an improperly wired outlet will cause the adapter fuse to blow and may damage the adapter or the
ventilator.
Automobile Cigarette Lighter Outlet Power Rating - Running a ventilator from an improperly rated
automobile cigarette lighter outlet (less than 20 amperes) may cause a fuse in the automobile to blow,
causing the ventilator and possibly other accessories in the automobile to stop operating.
Automobile Cigarette Lighter Adapter - Do not operate the ventilator from the Automobile Cigarette
Lighter Adapter while starting the vehicle or when jump starting the automobile battery. Doing so may
cause damage to the ventilator.
Automobile Cigarette Lighter Adapter Tip - Use care when disconnecting the Automobile Cigarette
Lighter Adapter after use, its tip may be hot.
Automobile Cigarette Lighter Outlet – Depending on the condition of the automobile battery,
whether the automobile is turned off, being started or running, automobile cigarette lighter outlets can
provide varying levels of voltage (in some, the outlet only operates when the vehicle is running).
Verify which power source the ventilator is using by checking the External Power LED on the
ventilator.
Remote Alarm - Always verify that the remote alarm properly reports the LTV®
 1200 / 1150 ventilator
alarms before use.
Remote Alarm - Always follow the remote alarm manufacturer’s usage and maintenance
requirements to guarantee proper function of the device. 
External Battery Pack - The External Battery Pack should only be connected to the LTV®
 1200 /
1150 ventilator using the CareFusion External Battery Cable (PN 10802). This cable is pre-wired and
properly terminated to ensure safe connection of the External Battery Pack to the ventilator.
Electrical Grounding – In the event of a loss of electrical protective ground, touching the ventilator
could result in electrical shock. To ensure grounding and avoid this danger, use only the unmodified
power cord originally supplied with the LTV®
 1200 / 1150 ventilator, maintained in good condition and
connected to a properly wired and grounded electrical power outlet.
Do not cover the ventilator – To avoid damage to the ventilator, do not cover while operating or
position relative to other objects such that the operation or performance of the ventilator may be
adversely affected. Ensure that sufficient space exists around the ventilator while in use to allow free
circulation of gases.
Electrostatic Discharge – The use of electrically conductive hoses and tubing is not recommended.
The use of such materials may result in damage to the ventilator from electrostatic discharge.
External DC Power Source or External Battery - When connecting the LTV®
 1200 / 1150 ventilator
to an external DC power source or external battery, use only the approved method and connectors
specified in Chapter 14 - Power and Battery Operation.
AC Power Source - When connecting the ventilator to an AC power source, use only the approved
LTV®
 AC Power Adapter.
AC Power Earth Ground Validity – If the validity of the AC power earth ground connection is in
doubt, use the internal battery, an external battery, or an external DC power source to operate the
LTV®
 1200 / 1150 ventilator.
Fuse Fire Hazard – Replacement of existing fuses with fuses with different voltage or electrical
current ratings may cause a fire.
Storage Temperature - Storing the LTV®
 1200 / 1150 ventilator at temperatures above 60°C (140°F)
for long periods can damage the internal battery and cause expected battery duration to degrade.
Patient Assist Call Connector – Do not apply more than 25V rms or 32VDC to the Patient Assist
Call connector.
Ventilator Checkout Tests - LTV®
 1200 / 1150 ventilator Checkout tests must be performed before
initial use of the ventilator. Rerun the tests whenever a question about the ventilator’s operation
arises.
Release Button - To avoid damaging the ventilator or the power connector, push the release button
on the connector before removing it from the ventilator power port or the power port pigtail connector. 
-->

## 2 Ventilator Overview

The {{vent}} ventilator system consists of:

1. Main ventilator unit containing sensors and valves
1. A single board computer control unit
1. User interface screen

The ventilator system has the following features:

* Low cost unit constructed from readily available parts in small lightweight package 
* Controllable from any device with a web browser (computer, tablet, phone, etc) secured via serial number and password. More than one ventilator can be monitored and controlled from a single display.
* Pressure Control ventilation mode
* Optional triggering based on patient inhalation attempt
* Oxygen enrichment based on a High-Pressure Oxygen source
* Monitors for {{fio2}}
* Real time displays of patient circuit pressure, flow and tidal volume
* Can be operated from AC, internal battery and external DC power sources

prototype-system-photo-1

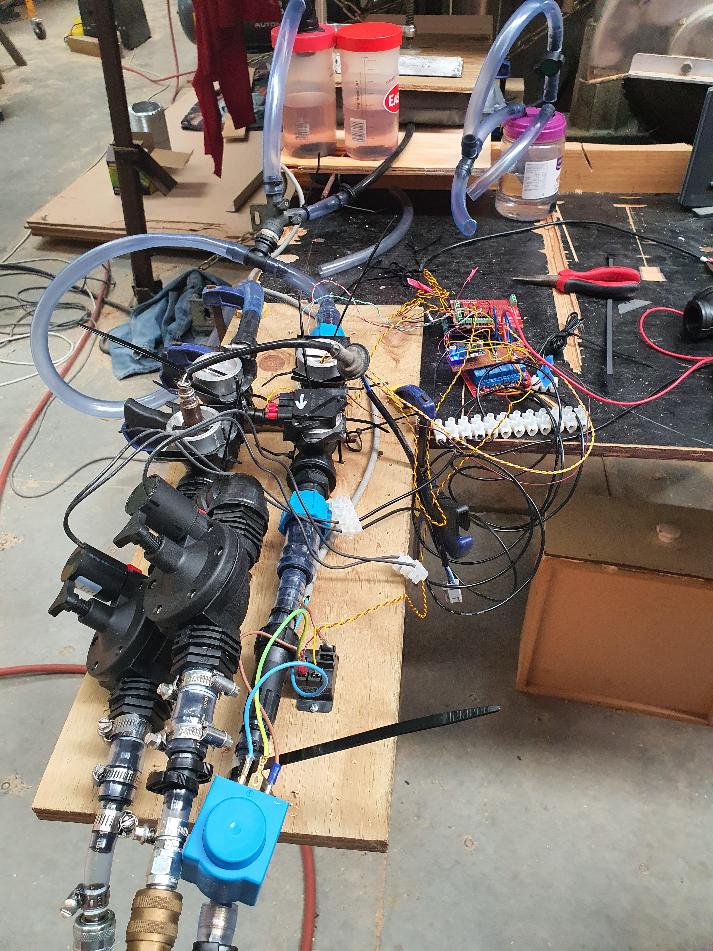
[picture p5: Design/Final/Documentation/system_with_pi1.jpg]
prototype-system-photo-2


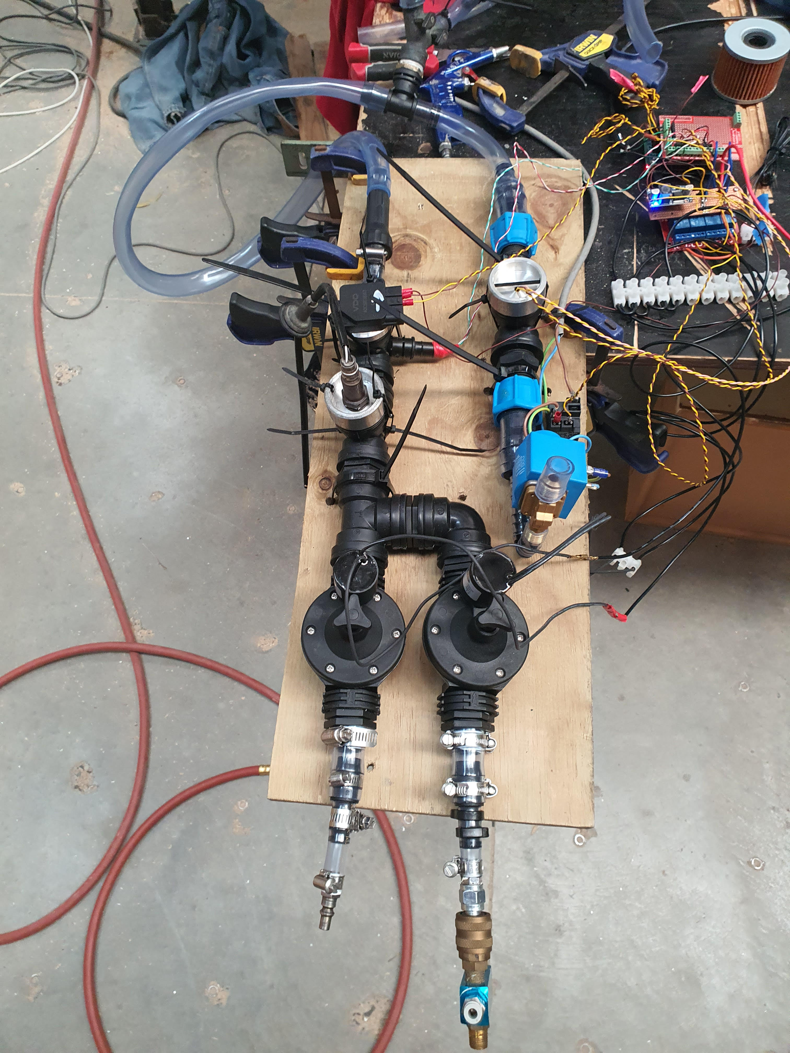
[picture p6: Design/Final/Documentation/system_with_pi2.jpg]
prototype-system-photo-3


ventilator-cad-1

ventilator-cad-iso

## 3 Breath Types

## 4 Ventilation Modes

## 5 Using the Controls and Indicators



<!--## Controls

## Displays and Indicators-->

## Ventilator Alarms

<!--## Extended Features-->

## Ventilator Checkout Tests

## Operating Procedure

Start the breathe app on the Raspbery pi.

```
$ python3 breathe.py
```

When `breathe` is started the flow meter configuration can be optionally supplied using the `--flow-meters` option, e.g. if both inhalation and exhalation flow meters are installed use:

```
$ python3 breathe.py --flow-meters=IE
```

## Cleaning, Disinfecting and Sterilizing

Do not immerse.

Remove solenoids and sensors from the ventilator. Autoclave ventialto as usual. 

Wipe solenoids and sensors down with appropriate sterilising solution.

<!-- ## Power and Battery Operation -->

## Troubleshooting

| Symptoms | Potential Causes | Operator Actions
| --- | --- | --- |
| xxx | yyy | zzz |

## Appendix A - Ventilator Specifications 

## Appendix B - Set Up / Maintenance 

## Appendix C - Installation and Checkout 

<!-- 

## Appendix D - Principles of Operation 

## Appendix E - Event Trace 

## Appendix F - Glossary 

## Appendix G - Index
-->

<!--

# Write.md

Go ahead, delete all the content in this document to get started writing your own.

 - To force save use CMD+S/CTRL+S
 - To open preview use CMD+I/CTRL+I
 - To share use https://writemd.xyz/p/5e82a1ffa27cc4670

## Contents

[TOC]

## Welcome
Welcome to Write.md, a place to write Markdown without any distractions. Your document is secured using AES 256 bit encryption and you can quickly share and collaborate using the URL in your address bar.

## Sharing & Collaboration
You can share this doc using https://writemd.xyz/d/5e82a1ffa27cc4670. Anyone that has access to your document URL can make changes that save/overwrite the original content, so be careful who you share with.

## Preview
You can enter preview of your document using https://writemd.xyz/p/5e82a1ffa27cc4670 - replacing the D for document in the URL with P for preview.

## Export & Print
You can export or print your document by firstly previewing the page (see Preview) and using your browsers default printing option which should allow you to export PDF, HTML or send to printer.

## Variables (new)

--var family_name: Dursley

When Mr and Mrs {{family_name}} woke up on the dull, grey Tuesday our story starts, there was nothing about the cloudy sky outside to suggest that strange and mysterious things would soon be happening all over the country. Mr {{family_name}} hummed as he picked out his most boring tie for work and Mrs {{family_name}} gossiped away happily as she wrestled a screaming Dudley into his high chair.

## Themes

You can set both the editor and preview pane theme by creating a new variable called `wmdEditorTheme` and `wmdPreviewTheme` and setting them anywhere in the page.

Heres an example of the default look, remove the space between -- and var to set.

```
-- var wmdPreviewTheme: default
-- var wmdEditorTheme: dark
```

The available themes are as follows:

### Editor Themes
- default
- 3024-day
- 3024-night
- ambiance
- ambiance-mobile
- base16-dark
- base16-light
- blackboard
- cobalt
- eclipse
- elegant
- erlang-dark
- lesser-dark
- mbo
- mdn-like
- midnight
- monokai
- neat
- neo
- night
- paraiso-dark
- paraiso-light
- pastel-on-dark
- rubyblue
- solarized
- the-matrix
- tomorrow-night-eighties
- twilight
- vibrant-ink
- xq-dark
- xq-light

### Preview Themes
- default
- dark

## Flow Charts
```flow
st=>start: Launch Write.md
op=>operation: Start Writing
cond=>condition: Success? 
e=>end: Awesome

st->op->cond
cond(yes)->e
cond(no)->op
```

## What is Markdown?
Markdown (MD) is a lightweight markup language with plain-text-formatting syntax. Its design allows it to be converted to many output formats, but the original tool by the same name only supports HTML. If you would like to see the cheatsheet for writing MD just click [here](https://github.com/adam-p/markdown-here/wiki/Markdown-Cheatsheet).

## Love Write.md?
Why not leave us a review on product hunt to let others know how much you enjoy using Write.md https://www.producthunt.com/posts/write-md

-->

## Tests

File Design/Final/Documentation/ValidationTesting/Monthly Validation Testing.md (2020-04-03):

# Validation Test

This test should be conducted on a minimum of a monthly basis. This test
ensures that the machine is running consistently and accurately.

1.  Setup

    a)  Connect the machine to pressurised oxygen and air supplies.
        Leave outlet of expiratory unconnected.
    b)  Connect auxiliary pressure gauges to the inspiratory outlet
        (patient end) and expiratory inlet (patient end).
    c)  Connect inspiratory and expiratory lines to y connection and
        then to a dummy set of lungs that can provide compliance.

1.  Pressure Set Point Testing

    a)  Run the system at the IP and PEEP set points outlined in the
        table below. Fill in the table recording the results of the
        tests. Record IP and PEEP both from the output graphs and from
        the auxiliary gauges.

IP SetPoint (cmH20) | PEEP SetPoint (cmH20) | IP from aux gauge (cmH20) | Percentage difference from set point (%) | PEEP fromaux gauge (cmH20) | Percentage difference from set point (%) | IP from graph (cmH20) | Percentage difference from aux gauge (%) | PEEP from graph (cmH20) | Percentage difference from aux gauge (%) | Tidal Volume from graph (ml) | Notes
-- | -- | -- | -- | -- | -- | -- | -- | -- | -- | -- | --
40 | 20 |   |   |   |   |   |   |   |   |   |  
35 | 15 |   |   |   |   |   |   |   |   |   |  
30 | 10 |   |   |   |   |   |   |   |   |   |  
25 | 5 |   |   |   |   |   |   |   |   |   |  
20 | 0 |   |   |   |   |   |   |   |   |   |  

1.  FiO2 Set Point Testing

    a)  Run the system at the FiO2 set points outlined in the table
        below. Fill in the table recording the results of the tests.

+-----------+-----------+-----------+-----------+-----------+-----------+
| IP Set    | PEEP Set  | FiO2 Set  | FiO2      | TV        | Notes     |
| Point     | Point     | Point     | Recorded  | recorded  |           |
|           | (cmH2O)   |           | from      | from      |           |
| (cmH20)   |           | (% O2)    | graph (%  | graph     |           |
|           |           |           | O2)       | (ml)      |           |
+-----------+-----------+-----------+-----------+-----------+-----------+
| 40        | 20        | 20        |           |           |           |
+-----------+-----------+-----------+-----------+-----------+-----------+
| 40        | 20        | 30        |           |           |           |
+-----------+-----------+-----------+-----------+-----------+-----------+
| 40        | 20        | 40        |           |           |           |
+-----------+-----------+-----------+-----------+-----------+-----------+
| 40        | 20        | 50        |           |           |           |
+-----------+-----------+-----------+-----------+-----------+-----------+
| 40        | 20        | 60        |           |           |           |
+-----------+-----------+-----------+-----------+-----------+-----------+
| 40        | 20        | 70        |           |           |           |
+-----------+-----------+-----------+-----------+-----------+-----------+
| 40        | 20        | 80        |           |           |           |
+-----------+-----------+-----------+-----------+-----------+-----------+
| 40        | 20        | 90        |           |           |           |
+-----------+-----------+-----------+-----------+-----------+-----------+
| 40        | 20        | 100       |           |           |           |
+-----------+-----------+-----------+-----------+-----------+-----------+

1.  B.P.M Set Point Testing

    a)  Run the system at the B.P.M set points outlined in the table
        below. Fill in the table recording the results of the tests.

+---------+---------+---------+---------+---------+---------+---------+
| IP Set  | PEEP    | B.P.M   | B.P.M   | Percent | TV      | Notes   |
| Point   | Set     | Set     | Recorde | age     | recorde |         |
|         | Point   | Point   | d       | differe | d       |         |
| (cmH20) | (cmH2O) |         | from    | nce     | from    |         |
|         |         |         | graph   | from    | graph   |         |
|         |         |         |         | set     | (ml)    |         |
|         |         |         |         | point   |         |         |
|         |         |         |         | to      |         |         |
|         |         |         |         | recorde |         |         |
|         |         |         |         | d       |         |         |
|         |         |         |         | B.P.M   |         |         |
|         |         |         |         | (%)     |         |         |
+---------+---------+---------+---------+---------+---------+---------+
| 40      | 20      | 5       |         |         |         |         |
+---------+---------+---------+---------+---------+---------+---------+
| 40      | 20      | 10      |         |         |         |         |
+---------+---------+---------+---------+---------+---------+---------+
| 40      | 20      | 15      |         |         |         |         |
+---------+---------+---------+---------+---------+---------+---------+
| 40      | 20      | 20      |         |         |         |         |
+---------+---------+---------+---------+---------+---------+---------+
| 40      | 0       | 5       |         |         |         |         |
+---------+---------+---------+---------+---------+---------+---------+
| 40      | 0       | 10      |         |         |         |         |
+---------+---------+---------+---------+---------+---------+---------+
| 40      | 0       | 15      |         |         |         |         |
+---------+---------+---------+---------+---------+---------+---------+
| 40      | 0       | 20      |         |         |         |         |
+---------+---------+---------+---------+---------+---------+---------+

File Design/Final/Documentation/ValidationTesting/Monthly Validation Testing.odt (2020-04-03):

Validation Test – Manawa Ora Ventilator

This test should be conducted on a minimum of a monthly basis. This test ensures that the machine is running consistently and accurately.

1. Setup
  a. Connect the machine to pressurised oxygen and air supplies. Leave outlet of expiratory unconnected.
  b. Connect auxiliary pressure gauges to the inspiratory outlet (patient end) and expiratory inlet (patient end).
  c. Connect inspiratory and expiratory lines to y connection and then to a dummy set of lungs that can provide compliance.
2. Pressure Set Point Testing
  a. Run the system at the IP and PEEP set points outlined in the table below. Fill in the table recording the results of the tests. Record IP and PEEP both from the output graphs and from the auxiliary gauges.

IP Set Point (cmH20) | PEEP Set Point (cmH20) | IP from aux gauge (cmH20) | Percentage difference from set point (%) | PEEP from aux gauge (cmH20) | Percentage difference from set point (%) | IP from graph (cmH20) | Percentage difference from aux gauge (%) | PEEP from graph (cmH20) | Percentage difference from aux gauge (%) | Tidal Volume from graph (ml) | Notes
40 | 20
35 | 15
30 | 10
25 | 5
20 | 0

3. FiO2 Set Point Testing
  a. Run the system at the FiO2 set points outlined in the table below. Fill in the table recording the results of the tests.

IP Set Point (cmH20) | PEEP Set Point (cmH2O) | FiO2 Set Point (% O2) | FiO2 Recorded from graph (% O2) | TV recorded from graph (ml) | Notes
40 | 20 | 20
40 | 20 | 30
40 | 20 | 40
40 | 20 | 50
40 | 20 | 60
40 | 20 | 70
40 | 20 | 80
40 | 20 | 90
40 | 20 | 100

4. B.P.M Set Point Testing
  a. Run the system at the B.P.M set points outlined in the table below. Fill in the table recording the results of the tests.

IP Set Point (cmH20) | PEEP Set Point (cmH2O) | B.P.M Set Point | B.P.M Recorded from graph | Percentage difference from set point to recorded B.P.M (%) | TV recorded from graph (ml) | Notes
40 | 20 | 5
40 | 20 | 10
40 | 20 | 15
40 | 20 | 20
40 | 0 | 5
40 | 0 | 10
40 | 0 | 15
40 | 0 | 20

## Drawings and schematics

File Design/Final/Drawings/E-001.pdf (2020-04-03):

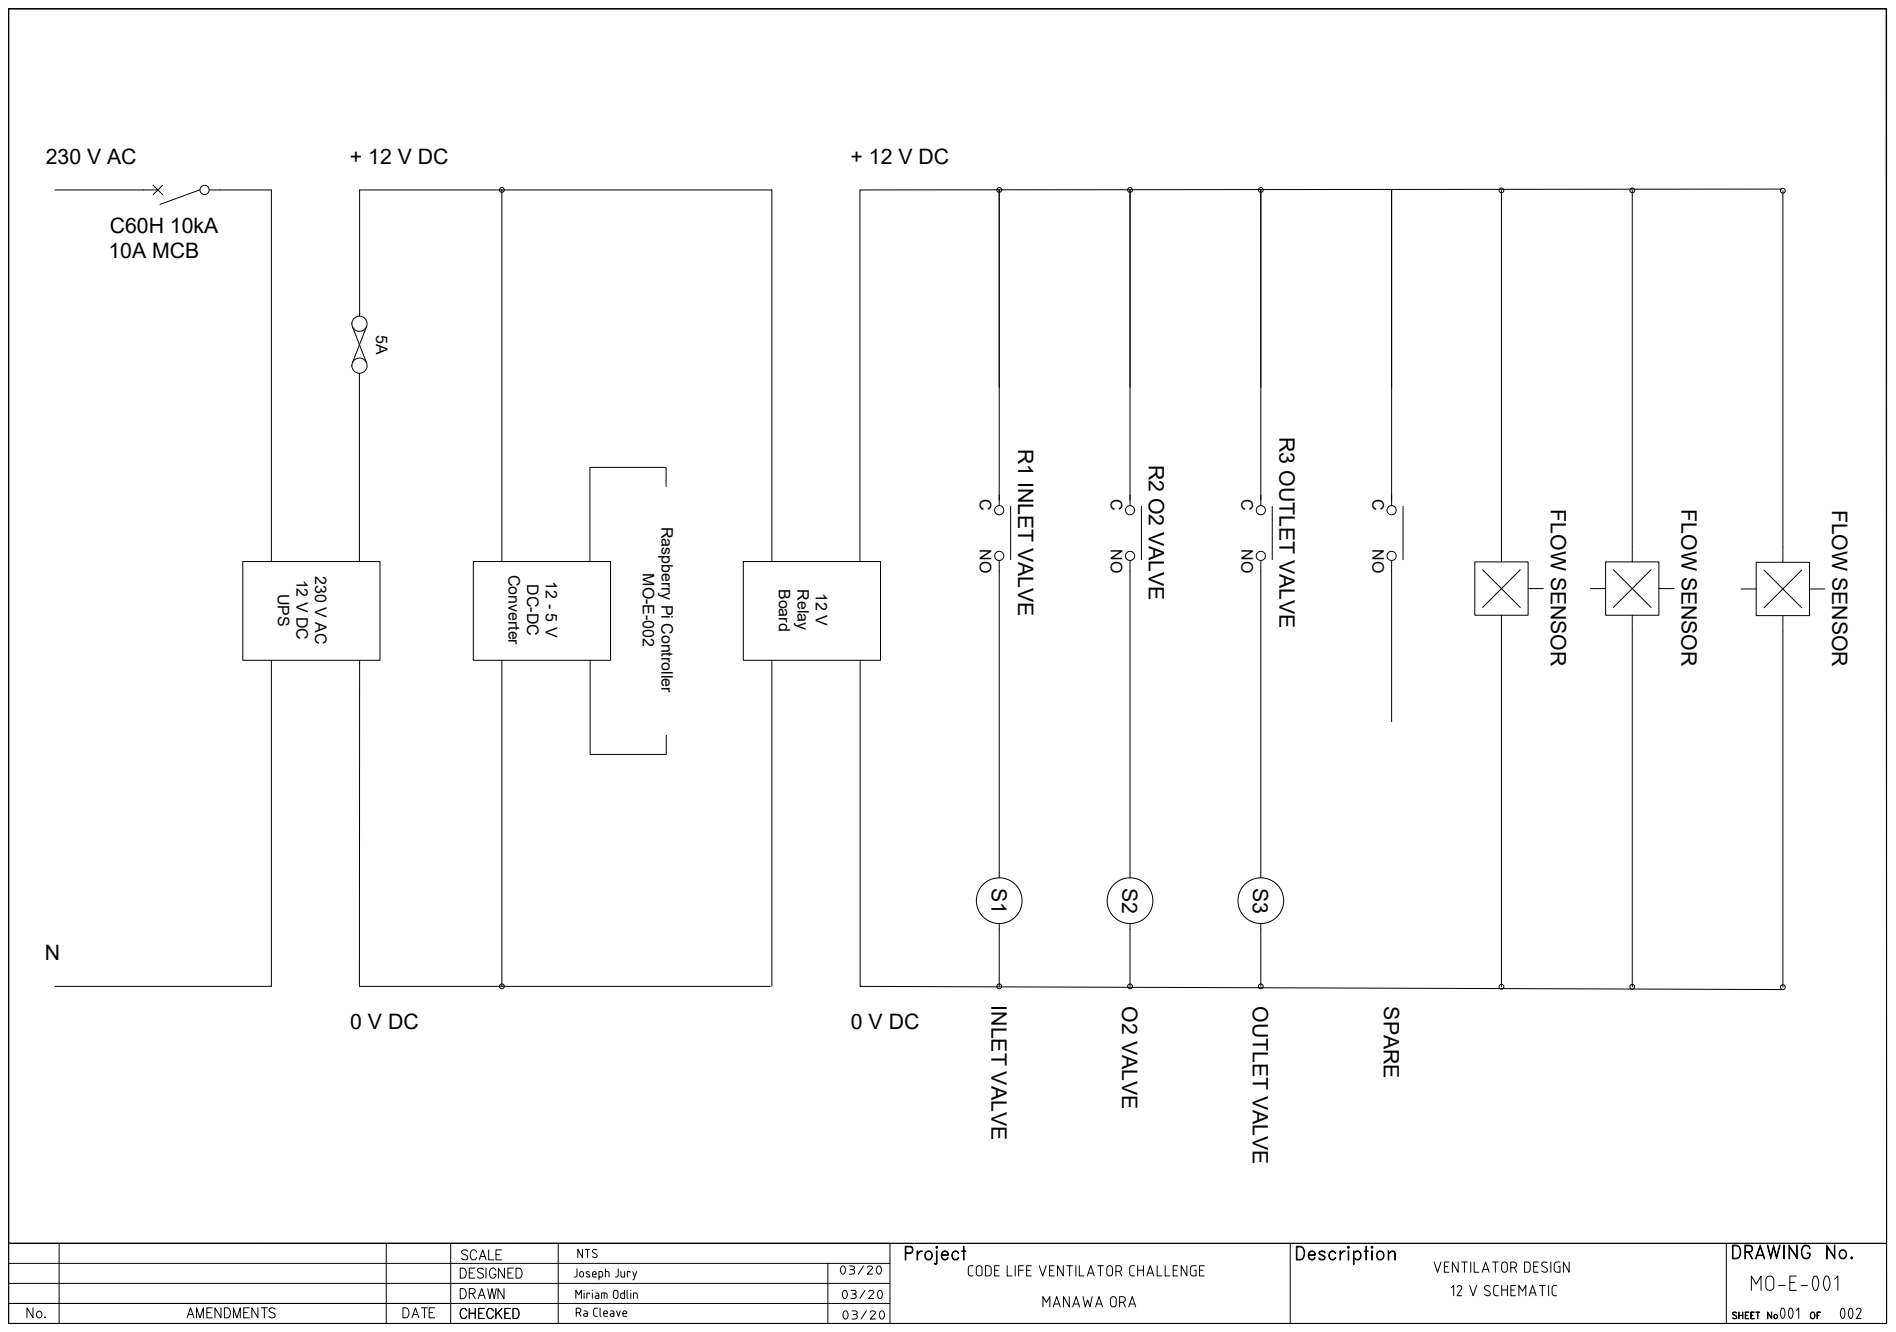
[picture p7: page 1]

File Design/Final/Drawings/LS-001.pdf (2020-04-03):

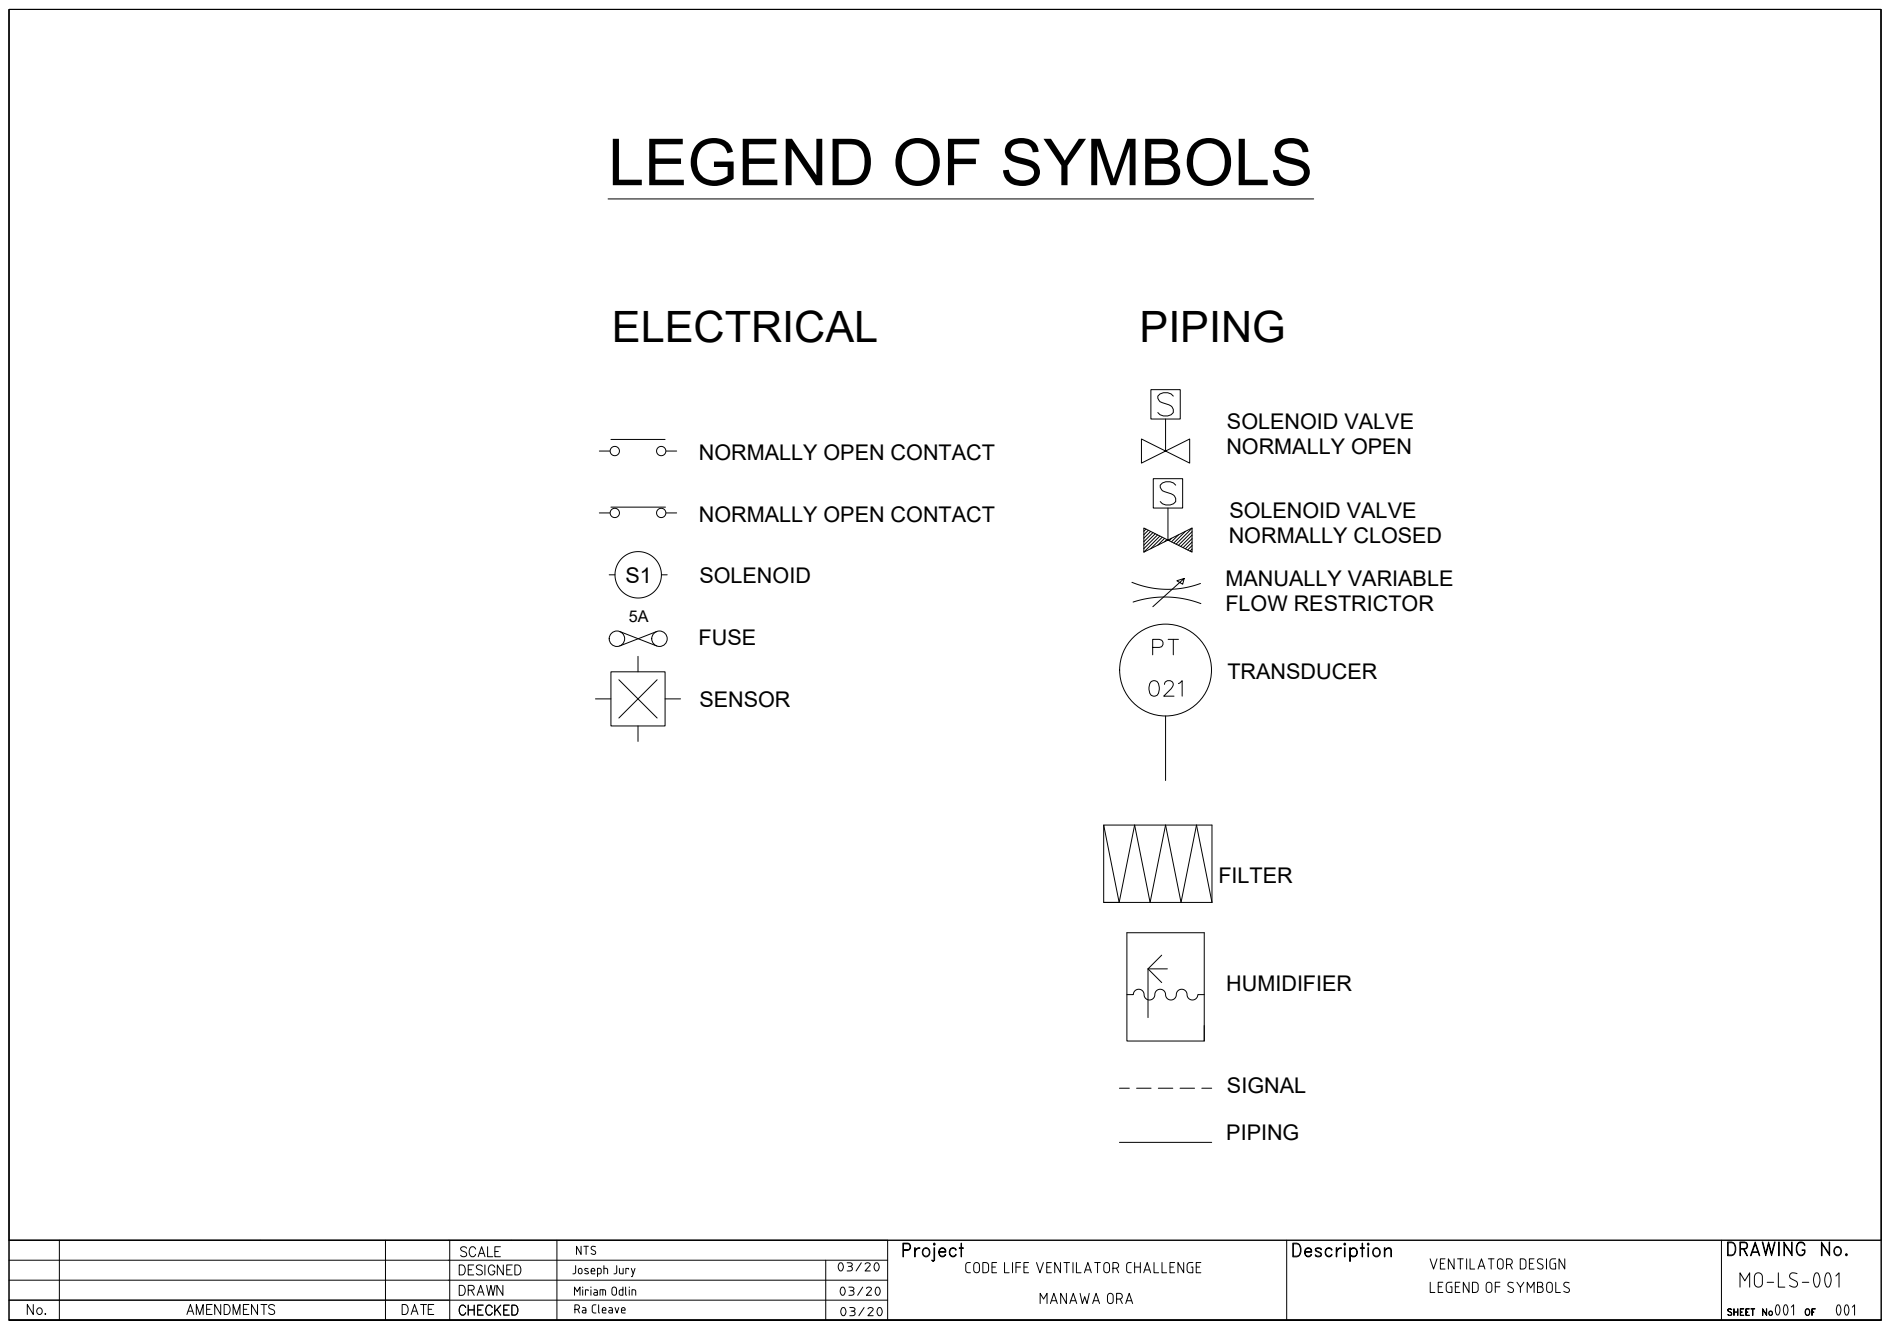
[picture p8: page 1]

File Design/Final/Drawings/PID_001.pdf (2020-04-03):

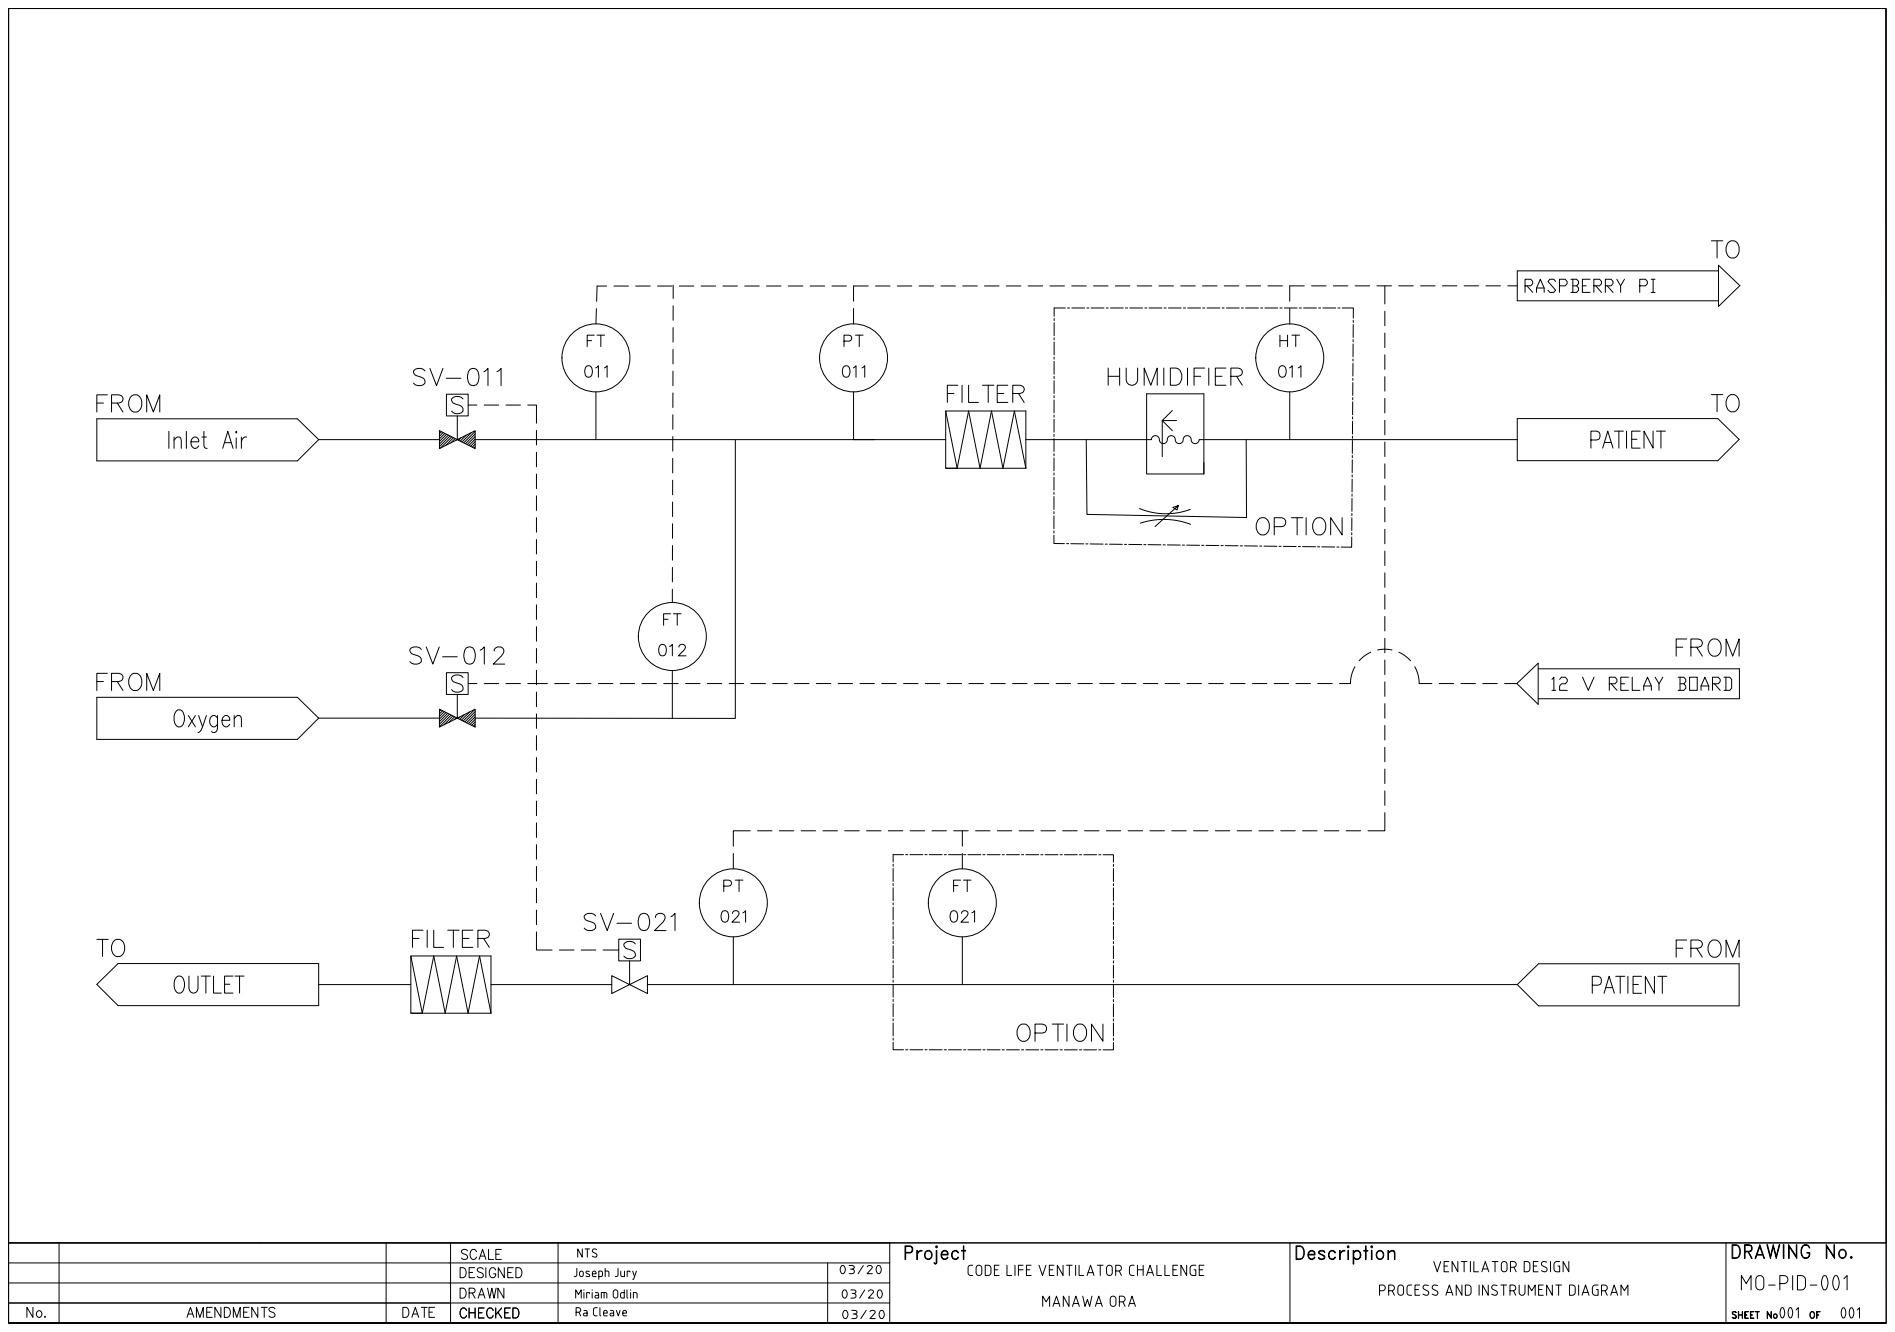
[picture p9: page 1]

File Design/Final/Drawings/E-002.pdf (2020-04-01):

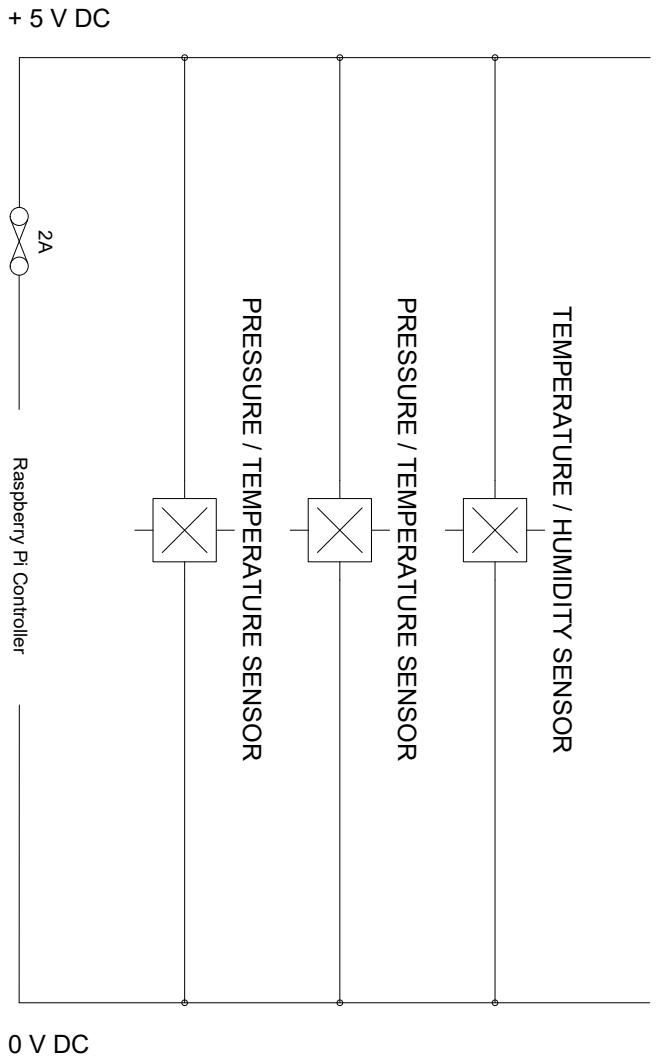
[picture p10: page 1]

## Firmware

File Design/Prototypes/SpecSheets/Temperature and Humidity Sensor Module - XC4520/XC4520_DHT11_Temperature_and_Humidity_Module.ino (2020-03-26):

//KY015 DHT11 Temperature and humidity sensor 
int DHpin = 8;
byte dat [5];
 
void setup () {
  Serial.begin (9600);
  pinMode (DHpin, OUTPUT);
}
 
void loop () {
  start_test ();
  Serial.print ("Current humdity =");
  Serial.print (dat [0], DEC); // display the humidity-bit integer;
  Serial.print ('.');
  Serial.print (dat [1], DEC); // display the humidity decimal places;
  Serial.println ('%');
  Serial.print ("Current temperature =");
  Serial.print (dat [2], DEC); // display the temperature of integer bits;
  Serial.print ('.');
  Serial.print (dat [3], DEC); // display the temperature of decimal places;
  Serial.println ('C');
  delay (700);
}

byte read_data () {
  byte data;
  for (int i = 0; i < 8; i ++) {
    if (digitalRead (DHpin) == LOW) {
      while (digitalRead (DHpin) == LOW); // wait for 50us
      delayMicroseconds (30); // determine the duration of the high level to determine the data is '0 'or '1'
      if (digitalRead (DHpin) == HIGH)
        data |= (1 << (7-i)); // high front and low in the post
      while (digitalRead (DHpin) == HIGH); // data '1 ', wait for the next one receiver
     }
  }
return data;
}
 
void start_test () {
  digitalWrite (DHpin, LOW); // bus down, send start signal
  delay (30); // delay greater than 18ms, so DHT11 start signal can be detected
 
  digitalWrite (DHpin, HIGH);
  delayMicroseconds (40); // Wait for DHT11 response
 
  pinMode (DHpin, INPUT);
  while (digitalRead (DHpin) == HIGH);
  delayMicroseconds (80); // DHT11 response, pulled the bus 80us
  if (digitalRead (DHpin) == LOW);
  delayMicroseconds (80); // DHT11 80us after the bus pulled to start sending data
 
  for (int i = 0; i < 4; i ++) // receive temperature and humidity data, the parity bit is not considered
    dat[i] = read_data ();
 
  pinMode (DHpin, OUTPUT);
  digitalWrite (DHpin, HIGH); // send data once after releasing the bus, wait for the host to open the next Start signal
}

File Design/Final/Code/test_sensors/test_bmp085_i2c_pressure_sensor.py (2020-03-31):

#!/usr/bin/python

import sys
sys.path.append('../')
from bmp085 import BMP085

import smbus
import time

bus = smbus.SMBus(1) # or bus = smbus.SMBus(1) if you have a revision 2 board 
address = 0x77


def read_byte(adr):
    return bus.read_byte_data(address, adr)

def read_word(adr):
    high = bus.read_byte_data(address, adr)
    low = bus.read_byte_data(address, adr+1)
    val = (high << 8) + low
    return val

def read_word_2c(adr):
    val = read_word(adr)
    if (val >= 0x8000):
        return -((0xffff - val) + 1)
    else:
        return val

def write_byte(adr, value):
    bus.write_byte_data(address, adr, value)

def twos_compliment(val):
    if (val >= 0x8000):
        return -((0xffff - val) + 1)
    else:
        return val

def get_word(array, index, twos):
    val = (array[index] << 8) + array[index+1]
    if twos:
        return twos_compliment(val)
    else:
        return val

calibration = bus.read_i2c_block_data(address, 0xAA, 22)

oss = 0

test = False

if test:
    ac1 =    408
    ac2 =    -72
    ac3 = -14383
    ac4 =  32741
    ac5 =  32757
    ac6 =  23153
    b1 =    6190
    b2 =       4
    mb =  -32768
    mc =   -8711
    md =    2868

    temp_raw = 27898 
    pressure_raw = 23843 

else:
    ac1 = get_word(calibration, 0, True)
    ac2 = get_word(calibration, 2, True)
    ac3 = get_word(calibration, 4, True)
    ac4 = get_word(calibration, 6, False)
    ac5 = get_word(calibration, 8, False)
    ac6 = get_word(calibration, 10, False)
    b1 =  get_word(calibration, 12, True)
    b2 =  get_word(calibration, 14, True)
    mb =  get_word(calibration, 16, True)
    mc =  get_word(calibration, 18, True)
    md =  get_word(calibration, 20, True)

    # Read raw temperature
    write_byte(0xF4, 0x2E)
    time.sleep(0.05)
    temp_raw = read_word_2c(0xF6)

    write_byte(0xF4, 0x34 + (oss << 6))
    time.sleep(0.05)
    pressure_raw = ((read_byte(0xF6) << 16) + (read_byte(0xF7) << 8) + (read_byte(0xF8)) ) >> (8-oss)


print("Raw temp:", temp_raw)
print("Raw pressure:", pressure_raw)


#Calculate temperature
x1 = ((temp_raw - ac6) * ac5) / 32768
x2 = (mc * 2048) / (x1 + md)
b5 = x1 + x2
t = (b5 + 8) / 16
print("Temp: ", t / 10.0, "degrees C")

b6 = b5 - 4000 ; print("b6 = ", b6)
x1 = int(b2 * int(b6 * b6) >> 12) >> 11 ; print("x1 = ",x1)
x2 = int(ac2 * b6) >> 11 ; print("b6x2 = ",x2)
x3 = x1 + x2 ; print("x3 = ",x3)
b3 = int((int(ac1 * 4 + x3) << oss) + 2) >> 2 ; print("b3 = ",b3)

x1 = int(ac3 * b6) >> 13 ; print("x1 = ",x1)
x2 = int(b1 * int(int(b6 * b6) >> 12)) >> 16 ; print("x2 = ",x2)
x3 = int((x1 + x2) + 2) >> 2 ; print("x3 = ",x3)
b4 = int(ac4 * (x3 + 32768)) >> 15 ; print("b4 = ",b4)
b7 = (pressure_raw - b3) * (int(50000) >> oss) ; print("b7 = ",b7)
if (b7 < 0x80000000):
    p = (b7 * 2) /b4 ; print("p = ",p)
else:
    p = (b7 / b4) *2 ; print("p1 = ",p)
x1 = (int(p) >> 8) * (int(p) >> 8) ; print("x1 = ",x1)
x1 = int(x1 * 3038) >> 16 ; print("x1 = ",x1)
x2 = int(-7357 * p) >> 16 ; print("x2 = ",x2)
p = p + (int(x1 + x2 + 3791) >> 4) ; print("pressure = ",p,"Pa")


pSensor_h = BMP085(bus=1, address=0x77)
p_h, t_h = pSensor_h.read()
print("From sensors.py: %f cm H2O, %f degC " % (p_h, t_h))
pSensor_l = BMP085(bus=4, address=0x77)
p_l, t_l = pSensor_l.read()
print("From sensors.py: %f cm H2O, %f degC " % (p_l, t_l))

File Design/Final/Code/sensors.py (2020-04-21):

"""
Acquire sensor data.

Sensor nomenclature:

- type: flow (q), pressure (p), temp (t), humidity (h), O2 (o) 
- location: high pressure (isnpiration), low pressure (expiration)

jh, Mar 2020


Ra would like:

sensors = [
 {'name': 'Insp. pressure', 
'sensor_type': 'bmp085', 
'read_fn': None, 
'last_val': None, 
'units': 'Pa', 
'alarm_low': None, 
'alarm_high': None},
...]

can have derived channels in this list using e.g. read_fn = random().
can then fill in read_fn based on sensor type, and loop through this in read_all? 
can also pass this whole array back to main, and fill in MQTT stream with at least (name, value, unit, alarm_status) for each channel.

"""
import threading
from datetime import timedelta
import collections
import time

#try:
#    from gpiozero import LED
#except:
#    from fakegpiozero import LED

from valve_drv import ValveDrvThread
from bmp085 import BMP085
from pidf import PIDF
from lpf import LPF
from rate_limiter import RateLimiter

try:
    from smbus import SMBus
except:
    from fakesmbus import SMBus
bus = SMBus(1)

# at the moment I'm hoping to simply grab everything once per control loop
# if it turns out sensors are slow/variable to read then this plan will change
__all__ = ["read_all", "Sensors"] 

bmp085_i = BMP085(bus=1, address=0x77)
bmp085_e = BMP085(bus=4, address=0x77)

# this device should be address 0x48
def read_ai0():
    try:
        bus.write_byte(0x48, 0 & 0x03) # select the channel
        bus.write_byte(0x48, 0) # give it time to convert
        return bus.read_byte(0x48)
    except IOError as e:
        print('Read AI error! ', e)
        return 31

def read_all():

    #from time import sleep
    #sleep(0.05) # hopefully 50ms is an over-estimate of the time it'll take to readout all the sensor info
    #from random import random


    #print('reading p_i')
    p_i, t_i = bmp085_i.read()
    #print('reading p_i')
    p_e, t_e = bmp085_e.read()
    # Scale factor, sf. 
    #sf = 5 # When sensor is on inspiratory line.
    sf = 10 # When sensor is on expiratory line.
    q_i = sf*(read_ai0() - 31) # 31 seems to be zero flow.
    #q_i = 0
    
    return {
        't': time.time(),
        'q_i': q_i,
        'q_e': None,
        'p_i': p_i, 
        'p_e': p_e,
        't_i': t_i,
        't_e': t_e,
        'o_i': None,
        'o_e': None,
    }


class SensorsThread(threading.Thread):
    def __init__(self, fs=10, daemon=True, maxnvalues=100, read_all_duration=0.11, **kwargs):
        threading.Thread.__init__(self)
        self.p_set_point = 0
        self.rl_p_set_point = RateLimiter(-50, 100, 1/30)
        self.rl_p = RateLimiter(-50, 100, 1/15)
        #self.rl_u = RateLimiter(-.25, .5, 1/15)
        self.rl_u = RateLimiter(-.1, .2, 1/15)
        #self.pidf = PIDF(0.4, 0, 0, 0.0)
        #self.pidf = PIDF(0.01, 0.008, 0, 0.00, iLimits=[0, .2], uLimits=[0, 10]) # ok
        self.pidf = PIDF(0.01, 0.01, 0.0, 0.002, iLimits=[0, .2], uLimits=[0, 10])
        # 2 Hz.
        #self.lpf_p = LPF([0.00355661, 0.00711322, 0.00355661], [ 1., -1.78994555,0.80417199])
        # 5 Hz at fs=15
        #[0.05628602, 0.16885807, 0.16885807, 0.05628602]
        self.lpf_p = LPF([ 0.02224617,  0.08898467,  0.13347701,  0.08898467,  0.02224617], [ 1.        , -1.18741255,  0.74859907, -0.23634219,  0.03109435])

        self.i_valve_id = 0
        self.e_valve_id = 2
        self.stopped = threading.Event()
        self.delay = timedelta(seconds=(max(0, 1./fs - read_all_duration)))
        print(self.delay)
        self.samples_recv = 0
        self.current_values = collections.deque(maxlen=maxnvalues)
        self.daemon = daemon # if set auto-terminate when main thread exits
        #self.valves = [LED(17), LED(18), LED(22)]
        self.inspiration = False # for tracking inspiration/expiration
        self.V = ValveDrvThread([17, 18, 22], fs=400)
        for k,v in kwargs.items():
            setattr(self, k, v) # e.g. installed_flow_meters
        self.start()
        

    def stop(self):
        self.stopped.set()
        self.join()

    #def send_to_valve(self, valve_id, signal):
    #    # Make some sort of PWM
    #    if signal > 0:
    #        self.valves[valve_id].on()
    #    else:
    #        self.valves[valve_id].off()
        
        
    def run(self):
        while not self.stopped.wait(self.delay.total_seconds()):
            current_val = read_all()
            if self.inspiration and len(self.current_values) > 0:
                if current_val['p_i'] < 0:
                    current_val['p_i'] = self.current_values[-1]['p_i']
                if current_val['p_e'] < 0:
                    current_val['p_e'] = self.current_values[-1]['p_e']
                    
            #current_val['ie'] = self.ie # not needed, but maybe helpful for debugging

            # integrate tidal volume
            if len(self.current_values)>1: # catch the case when no data yet acquired
                dt = current_val['t'] - self.current_values[-1]['t']
                dtv = (current_val['q_i'] + self.current_values[-1]['q_i'])/2 * dt
                if self.installed_flow_meters=='I':
                    if self.inspiration:
                        current_val['tv_i'] = self.current_values[-1]['tv_i'] + dtv
                    else:
                        current_val['tv_i'] = 0 # FIXME: patient exhales instantaneously!!!
                elif self.installed_flow_meters=='E':
                    if self.inspiration:
                        # start simple with just -ve 
                        current_val['tv_i'] = 0 # FIXME: patient INHALES instantaneously!!!
                    else:
                        current_val['tv_i'] = self.current_values[-1]['tv_i'] + dtv
                else:
                    raise ValueError('Unknown value for installed_flow_meters=%s % self.installed_flow_meters')
            else:
                current_val['tv_i'] = 0 # default value
            
            if self.inspiration or True:
                p_set_point_rl = self.rl_p_set_point.update(self.p_set_point)
            else:
                p_set_point_rl = self.p_set_point
            #p_set_point_rl = self.p_set_point
            #print(p_set_point_rl)
            y = self.rl_p.update(current_val['p_e'])
            y = self.lpf_p.update(y)
            current_val['y'] = y
            current_val['y_s'] = p_set_point_rl
            current_val['u'] = self.pidf.calc_output(y, p_set_point_rl)
            current_val['u_f'] = self.rl_u.update(current_val['u'])
            #print('%.3f' % current_val['u'])

            #print('%2.0f\t%2.0f\t%2.0f' % (self.p_set_point, self.current_values[-1]['p_i'] - 988, u))
            #print(' '*2*int(p_set_point_rl) + 's')
            #print(' '*2*int(self.current_values[-1]['p_i']) + 'p')
            #print(' '*int(u) + 'u')
            
            # Send control signals to valves.
            if self.inspiration:
                self.V.u[0] = current_val['u_f']
                self.V.u[2] = 0
            else:
                #self.V.u[0] = 0
                self.V.u[0] = current_val['u_f']
                self.V.u[2] = 1
                #if current_val['p_e'] > p_set_point_rl:
                #    self.V.u[2] = 1
                #else:
                #    self.V.u[2] = 0
            
            self.current_values.append(current_val)
            self.samples_recv += 1

            
if __name__=="__main__":
    #T = SensorsThread(fs=10, daemon=False)
    print(read_bmp085_i(0x77))
        

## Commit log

2020-03-23 Parts list for repurposed valves and computer concept
    [VentilatorParts.xlsx]
2020-03-24 editing spreadsheet
    [VentilatorParts.xlsx]
2020-03-24 Updated with pressure and flow sensors
    [VentilatorParts.xlsx]
2020-03-25 Created 'purchased inventory' Sheet in VentilatorParts
    [VentilatorParts.xlsx]
2020-03-25 Adding Ra's plunder of 25/3 to the inventory list
    [VentilatorParts.xlsx]
2020-03-25 Moving inventory list to Design/Prototypes directory
    [InventoryList.xlsx, VentilatorParts.xlsx]
2020-03-25 add sprinkler SHop parts
    [InventoryList.xlsx]
2020-03-26 Raspberry stuff
2020-03-26 More Raspberry stuff
2020-03-26 updated inventory list
    [InventoryList.xlsx]
2020-03-27 Pressure sensor test
2020-03-27 NEW sensors module
2020-03-27 Updated inventory and a couple of websites about MAF sensor.
    [InventoryList.xlsx]
2020-03-27 threaded control app skeleton
2020-03-28 ENH ring buffer sensor readings
2020-03-28 Reorganisation of repo
    [VentilatorParts.xlsx]
2020-03-28 Pressure sensor cross check
2020-03-29 Actuated exh valve
2020-03-31 FIX catch the no data yet case
2020-03-31 Added Manufacturing BOM
    Needs additions From Ra for electrical stuff
    [Manufacturing BOM.xlsx]
2020-03-31 Inspection test plan and inspection test reports
    need to be completed
    [Test Plan and Results.xlsx]
2020-03-31 First cut at CAD
2020-03-31 Modified prototype BOM, made basic model BOM
    [Manufacturing BOM - Basic model.xlsx, Manufacturing BOM - Prototype.xlsx]
2020-03-31 ENH flow meter options
2020-04-01 Miriam's stuff
    [InputOutput.ods, VentElec1.dwg]
2020-04-01 New CAD files
    [Manufacturing BOM.xlsx]
2020-04-01 latest elec and PID drawings
    [VentElec1.dwg]
2020-04-03 Trying to regain some sense of sync
    [Test Plan and Results.xlsx]
2020-04-04 Technical note summarising work to date, some reorganisation.
    [InputOutput.ods, Manufacturing BOM - Basic model.xlsx, Manufacturing BOM - Prototype.xlsx, Test Plan and Results.xlsx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]
2020-04-21 PWM drive for inlet valve. Insp. pressure and PEEP much better.
